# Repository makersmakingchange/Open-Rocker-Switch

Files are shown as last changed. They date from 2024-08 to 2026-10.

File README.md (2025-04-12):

<!--- Open Source Assistive Technology: GitHub Readme Template Version 1.2 (2024-May-27)  --->
<!---
This is a GitHub repository intended to act as a template for an open source assistive technology device. It is meant to contain all design files, build files, and documentation for the project. More information about how to use the template is available in the [Documentation_Guide](/Documentation_Guide.docx). You can see examples of other Open AT Devices at the Makers Making Change [website](https://www.makersmakingchange.com/s/category/assistive-devices). 
--->
 
<!--- TITLE --->
# Open Rocker Switch
<!--- Should match the name of the GitHub repository. Choose something descriptive rather than whimsical.  --->

## Overview
<!--- A brief summary of the project. What it does, who it is for, how much it costs. --->
The Open Rocker Switch is an inexpensive 3D printable accessibility switch. The switch consists of two separate buttons that are activated by pressing on either side. This switch is comparable in size, activation force, and travel to the discontinued AbleNet Rocker Switch. The Open Rocker Switch has interchangeable button pieces and center divider pieces for users to customize and personalize their switch.

The device is comprised of off-the-shelf electronics and 3D printed parts. 

The Open Rocker Switch is open assistive technology (OpenAT). Under the terms of the open source licenses, the device may be built, used, and improved upon by anyone.

The overall cost of materials is about $14 (plus $8 for component shipping).

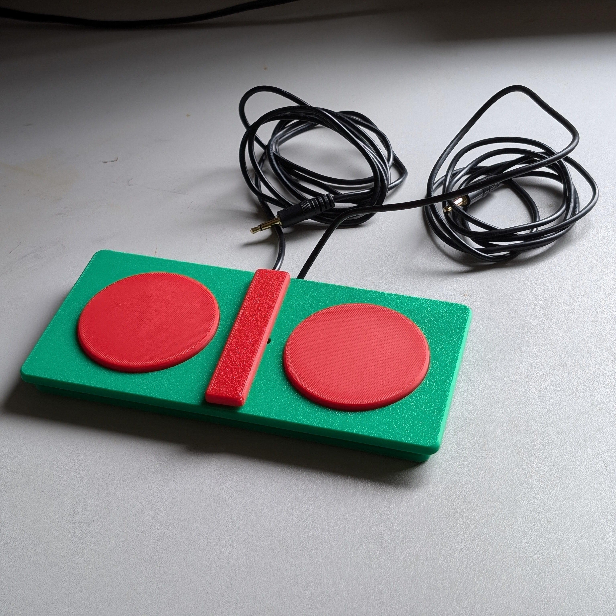
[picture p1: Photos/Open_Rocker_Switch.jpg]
Picture of Open Rocker Switch.


## Makers Making Change Assistive Device Library
https://www.makersmakingchange.com/s/product/open-rocker-switch/01tJR000000693uYAA

## How to Obtain the Device
### 1. Do-it-Yourself (DIY) or Do-it-Together (DIT)

This is an open-source assistive technology, so anyone is free to build it. All of the files and instructions required to build the device are contained within this repository. Refer to the Maker Guide below.

### 2. Request a build of this device

You may also submit a build request through the [Makers Making Change Assistive Device Library Listing](https://www.makersmakingchange.com/s/product/open-rocker-switch/01tJR000000693uYAA) to have a volunteer maker build the device. As the requestor, you are responsible for reimbursing the maker for the cost of materials and any shipping.

### 3. Build this device for someone else

If you have the skills and equipment to build this device, and would like to donate your time to create the device for someone who needs it, visit the [MMC Maker Wanted](https://makersmakingchange.com/maker-wanted/) section.

## Build Instructions
<!--- Outline the major steps required to create a build --->

### 1. Read through the Maker Guide

The [Maker Guide](/Documentation/Open_Rocker_Switch_Maker_Guide.pdf)  contains all the necessary information to build this device, including tool lists, assembly instructions, programming instructions (if applicable) and testing.

### 2. Order the Off-The-Shelf Components
The [Bill of Materials](/Documentation/Open_Rocker_Switch_BOM.xlsx) lists all of the parts and components required to build the device.

### 3. Print the 3D Printable components
All of the files and individual print files can be found in the [/Build_Files/3D_Printing_Files](/Build_Files/3D_Printing_Files/) folder.

### 4. Assemble the Open Rocker Switch
Reference the Assembly Guide section of the [Maker Guide](/Documentation/Open_Rocker_Switch_Maker_Guide.pdf) for the tools and steps required to build the device.

## How to improve this Device
As open source assistive technology, you are welcomed and encouraged to improve upon the design. 

## Files
### Documentation
<!--- Update the name, link, and version for documentation --->
| Document             | Version | Link |
|----------------------|---------|------|
| Design Rationale     | 2.2     | [Open_Rocker_Switch_Design_Rationale](/Documentation/Open_Rocker_Switch_Design_Rationale.pdf)     |
| Maker Guide          | 2.2     | [Open_Rocker_Switch_Maker_Guide](/Documentation/Open_Rocker_Switch_Maker_Guide.pdf)     |
| Bill of Materials    | 2.2     | [Open_Rocker_Switch_Bill_of_Materials](/Documentation/Open_Rocker_Switch_BOM.xlsx)     |
| User Guide           | 2.2     | [Open_Rocker_Switch_User_Guide](/Documentation/Open_Rocker_Switch_User_Guide.pdf)    |
| Changelog            | 2.2     | [Changelog](CHANGES.txt)     |

### Design Files
<!--- Include a copy of the original design files to facilitate easy editing and customization. Consider also including a generic format (e.g., STEP) --->
 - [CAD Files](/Design_Files/CAD_Design_Files)

### Build Files
<!--- Include a copy of the build files intended for manufacturing. This may include svg files for laser cutting, stl files for 3d printing, Gerber files for custom PCBs, and Arduino files for custom firmware. --->
 - [3D Printing Files](/Build_Files/3D_Printing_Files)

## License
<!--- Add the year(s) for the copyright and the Designer Name. You may use the standard set of open licenses or choose your own for the hardware, software, and accompanying materials. --->
Copyright (c) 2024 Neil Squire Society.

This repository describes Open Hardware:
 - Everything needed or used to design, make, test, or prepare the Open Rocker Switch is licensed under the [CERN 2.0 Weakly Reciprocal license (CERN-OHL-W v2) or later](https://cern.ch/cern-ohl ) .
 - Accompanying material such as instruction manuals, videos, and other copyrightable works that are useful but not necessary to design, make, test, or prepare the <Device-Name> are published under a [Creative Commons Attribution-ShareAlike 4.0 license (CC BY-SA 4.0)](https://creativecommons.org/licenses/by-sa/4.0/) .

You may redistribute and modify this documentation and make products using it under the terms of the [CERN-OHL-W v2](https://cern.ch/cern-ohl).
This documentation is distributed WITHOUT ANY EXPRESS OR IMPLIED WARRANTY, INCLUDING OF MERCHANTABILITY, SATISFACTORY QUALITY AND FITNESS FOR A PARTICULAR PURPOSE.
Please see the CERN-OHL-W v2 for applicable conditions.

Source Location: https://github.com/makersmakingchange/Open-Rocker-Switch

## Attribution
<!--- Provide any necessary attribution for designs or components that are included in the device or as part of the project. --->
The device was designed by Neil Squire Society/Makers Making Change. 

<!--- This is the attribution for the template. --->
The documentation template was created by Makers Making Change / Neil Squire Society and is used under a CC BY-SA 4.0 license. It is available at the following link: [https://github.com/makersmakingchange/OpenAT-Template](https://github.com/makersmakingchange/OpenAT-Template)

### Contributors
<!--- List the names of the people that contributed to the design. This could include the original source of the idea, designers, testers, documenters, etc. --->
Designers:
 - Gabriel Chu
 - Jake McIvor
 - Brad Wellington

---

<!-- ABOUT MMC START -->
## About Makers Making Change
[Makers Making Change Logo](https://www.makersmakingchange.com/)

Makers Making Change is a program of [Neil Squire](https://www.neilsquire.ca/), a Canadian non-profit that uses technology, knowledge, and passion to empower people with disabilities.

Makers Making Change leverages the capacity of community based Makers, Disability Professionals and Volunteers to develop and deliver affordable Open Source Assistive Technologies.

 - Website: [www.MakersMakingChange.com](https://www.makersmakingchange.com/)
 - GitHub: [makersmakingchange](https://github.com/makersmakingchange)
 - Bluesky: [@makersmakingchange.bsky.social](https://bsky.app/profile/makersmakingchange.bsky.social)
 - Instagram: [@makersmakingchange](https://www.instagram.com/makersmakingchange)
 - Facebook: [makersmakechange](https://www.facebook.com/makersmakechange)
 - LinkedIn: [Neil Squire Society](https://www.linkedin.com/company/neil-squire-society/)
 - Thingiverse: [makersmakingchange](https://www.thingiverse.com/makersmakingchange/about)
 - Printables: [MakersMakingChange](https://www.printables.com/@MakersMakingChange)

### Contact Us
For technical questions, to get involved, or to share your experience we encourage you to [visit our website](https://www.makersmakingchange.com/) or [contact us](https://www.makersmakingchange.com/s/contact).
<!-- ABOUT MMC END -->

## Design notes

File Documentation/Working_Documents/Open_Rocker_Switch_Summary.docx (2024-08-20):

# Overview

The Device Summary is intended to be a detailed summary of the device, product and maker information for the Open Rocker Switch, making it easier to add to the Makers Making Change website. It is intended for anyone who will view the device listing.

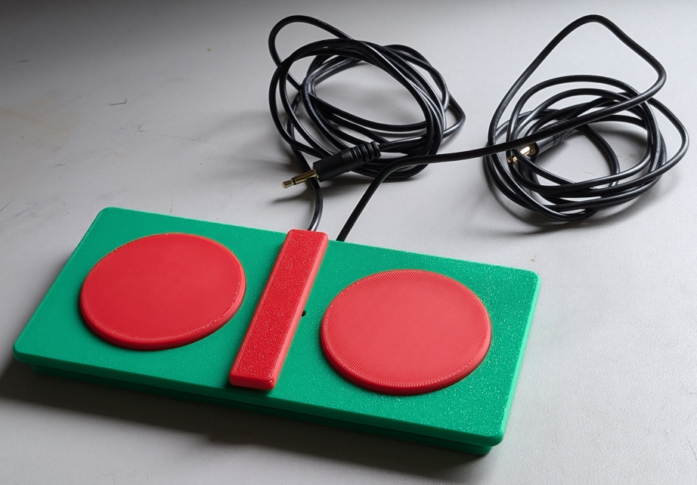
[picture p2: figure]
A photo of the Open Rocker Switch printed in green with red buttons and dividers

# Product Information

## Product Name

Open Rocker Switch

## Device Category

Mark any relevant categories with an “X”:

| Adapted Toys
| Aids for Daily Living (ADL)
X | Assistive Switches
X | Communication Aids (AAC)
X | Computer Access
| Environmental Controls
| Gaming
| Keyguard
| Kits
| LipSyncs
| Mounting
| Recreation and Leisure
| Seating and Positioning
| Switch Interfaces
| Writing Aids

## User Value Statement

If you are looking for an assistive switch to control two separate inputs on an accessible device, the dual action Open Rocker Switch might just be the two-in-one solution for you.

## Designer

Makers Making Change

# Device Information

## Overview

The Open Rocker Switch is a cost effective, 3D printed, dual action rocker switch that allows users to control dual input accessible devices.

# This switch is comparable in size, activation force, and travel to the discontinued AbleNet Rocker Switch. The Open Rocker Switch has interchangeable button pieces and center divider pieces for users to customize and personalize their switch.

## Disability Type

Select one or more disability types and mark with an “X”:

X | Agility / Dexterity
| Arthritis
X | Cognitive
| Hearing
X | Mobility
| Pain
| SCI
| Vision
| Other

## Disability Type Description

This device is designed for users of accessible switches, particularly those using devices that require dual inputs, such as scanning devices or morse code input.

## How To Use

The user presses on the buttons on either side of the central divider. The buttons activate the device connected to the corresponding mono cable.

## Estimated Cost

The estimated material cost of the device for a single build:

| $0 - $10
X | $11 - $25
| $26 - $50
| $51 - $100
| $101 - $250
| $250+

## Attribution

The Open Rocker Switch is inspired by the design of the now discontinued Ablenet Rocker Switch, originally created by TASH.

Design:

- Gabriel Chiu
- Jake McIvor
- Brad Wellington

# This switch is comparable in size, activation force, and travel to the discontinued AbleNet Rocker Switch. The Open Rocker Switch has interchangeable button pieces and center divider pieces for users to customize and personalize their switch.

# Maker Information

## Project Skills

Mark the required project skills with an “X”:

X | 3D Printing
| Custom PCB
| Electronics
| Laser Cutting
| Mechanics
| Software
X | Soldering
| Woodworking
| Other

## Skills Description

Hot glue to attach the buttons, 3D printing to create the components, soldering to attach the buttons to the cable, hand tools to trim parts and strip wires.

## Tools Needed

X | 3D Printer
X | Common Hand Tools
| Common Power Tools
| Laser Cutter
X | Soldering Iron
| Specialized Tooling

## Print time (hrs)

3

## Assembly time (hrs)

0.25

## Build Instructions

All parts are 3D printed. The buttons are bent and trimmed to shape, then the mono cables soldered to them. The buttons are hot glued to the switch base, then the cables cable tied in place. The buttons prints and divider are attached to the top rocker face of the switch, then the top face is connected to the bottom using the axle pin.

## Download Link

https://github.com/makersmakingchange/Open-Rocker-Switch /archive/refs/heads/main.zip

## Project Link

https://github.com/makersmakingchange/Open-Rocker-Switch

# License

## License

Hardware: CERN 2.0 Permissive license

Documentation: Creative Commons Attribution-ShareAlike 4.0

© 2024 by Neil Squire. This work is licensed under the CC BY SA 4.0 License: http://creativecommons.org/licenses/by-sa/4.0 Page 1 of 2

V2.2 | August 2024 Open Rocker Switch Summary

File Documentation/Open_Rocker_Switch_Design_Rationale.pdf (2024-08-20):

V2.2 | August 2024

## Open Rocker Switch

## DESIGN RATIONALE

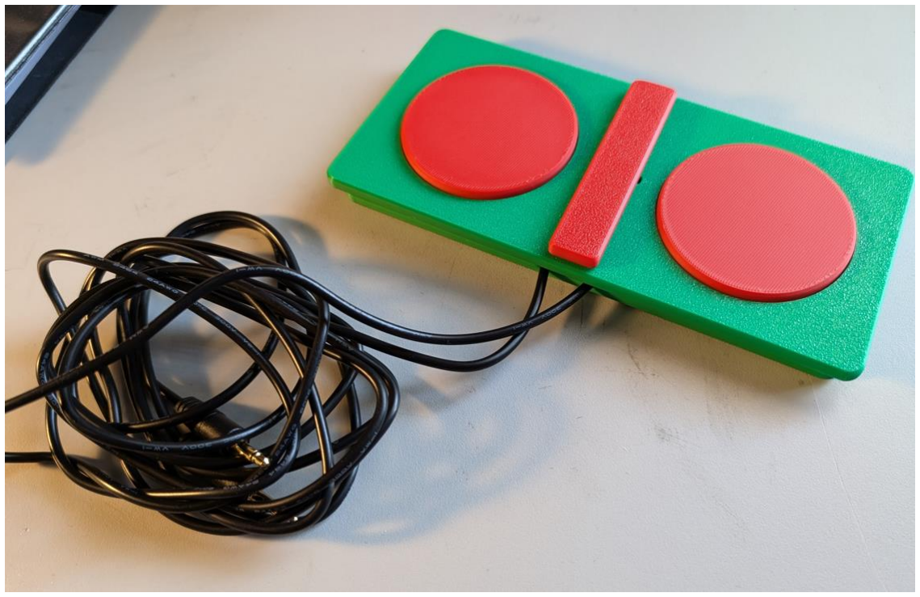
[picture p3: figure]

© 2024 by Neil Squire. (https://neilsquire.ca/)
This work is licensed under the CC BY SA 4.0 License: http://creativecommons.org/licenses/by-sa/4.0
Files available at https://github.com/makersmakingchange/Open-Rocker-Switch | Page 1 of 17

### Overview

The Design Rationale is intended to provide designers and maker information about the design process and design decisions behind the development of the Open Rocker Switch, a dual action rocker switch that is comparable in size, activation force, and travel to the discontinued AbleNet Rocker Switch

## DESIGN RATIONALE

Files available at https://github.com/makersmakingchange/Open-Rocker-Switch | Page 2 of 17

### Contents

Completion Checklist (DELETE BEFORE POSTING) | Error! Bookmark not defined.
Outline | 1
Introduction | 3
Research | 3
Requirements | 3
Goals | 3
Functional Requirements | 3
Non-functional Requirement | 3
Constraints | 3
Ideation | 4
Conceptual Design | Error! Bookmark not defined.
Concept 1 | Error! Bookmark not defined.
Concept 2 | Error! Bookmark not defined.
Concept 3 | Error! Bookmark not defined.
Prototyping | Error! Bookmark not defined.
Testing | 10
Detailed Design | 10
Opportunities for Improvement | Error! Bookmark not defined.

## DESIGN RATIONALE

Files available at https://github.com/makersmakingchange/Open-Rocker-Switch | Page 3 of 17

### Introduction

This design rationale is being put together for V2.2 of the device, and some information from the development has been lost.

A user of the AbleNet Rocker Switch was looking for a replacement switch after the one they were using was broken, but AbleNet had discontinued the switch. The Open Rocker Switch was developed as a open source replacement to meet the users needs.

The Open Rocker Switch is a low profile, low force switch that allows for controlling a device that requires multiple inputs, such as a scanning device or morse code input.

### Requirements

### Goals

G01 Open source switch comparable to the AbleNet Rocker Switch

### Functional Requirements

F01 | Same profile as the rocker switch
F02 | Same activation travel
F03 | Same activation force

### Non-functional Requirement

NF01 All parts must be available from the same supplier

### Constraints

C01 | Must be 3D printed
C02 | Must be manufacturable with common hand tools

### Commercially Available Options

Options that can be purchased but not made by a maker.

AbleNet Rocker Switch
Title / Name of device | Rocker Switch
Link | Discontinued
Author | AbleNet
Cost | $110 USD

## DESIGN RATIONALE

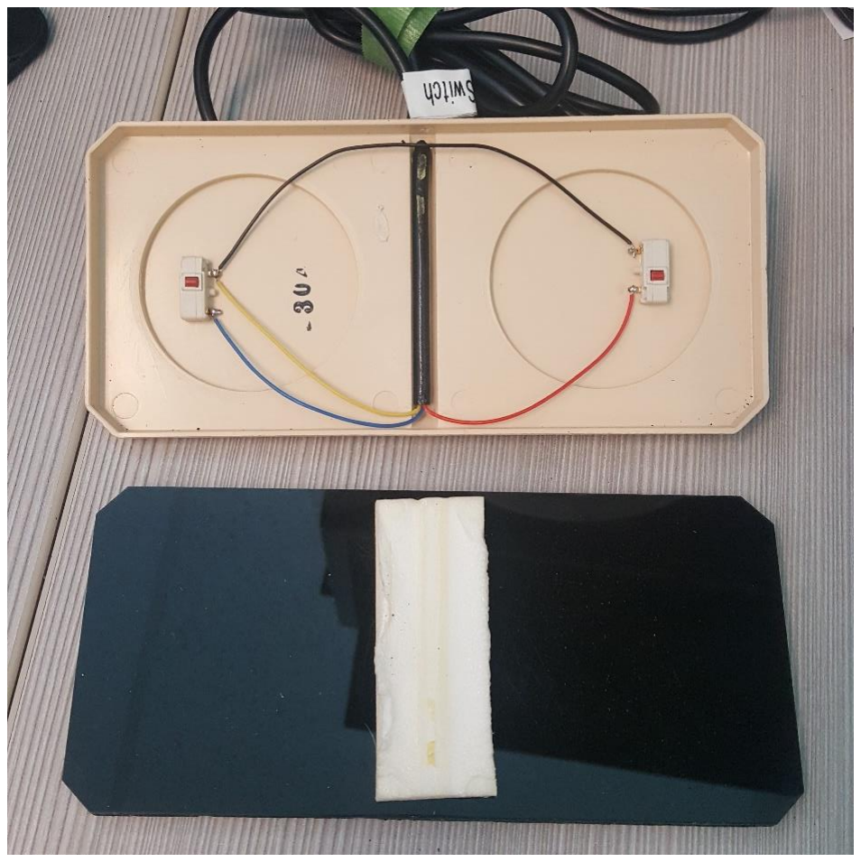
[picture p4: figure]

Files available at https://github.com/makersmakingchange/Open-Rocker-Switch | Page 4 of 17

The Rocker switch consisted of a base piece of acrylic, with a piece of two sided tape that acted as both an axle and a fixture for both sides. Two small switches were placed on the top under the buttons, and a stereo cable carried the signal out of the device.

Requirements Met | Requirements Unmet
The design of this device drove all requirements for the Open Rocker Switch | Availability

Useful Design Features
The user liked this device because it was low profile and low force, with two switch outputs.

### Ideation

The following is a compilation of all documents found in the ideation folder for this device.

## DESIGN RATIONALE

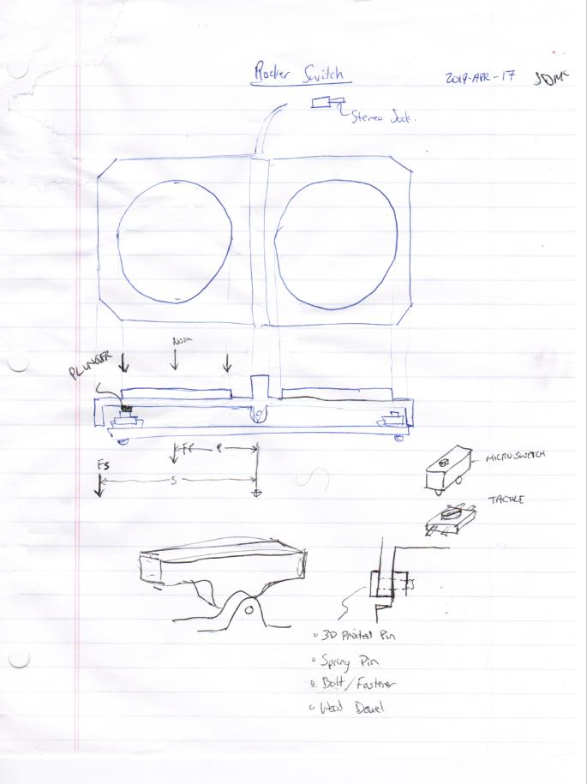
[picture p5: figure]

Files available at https://github.com/makersmakingchange/Open-Rocker-Switch | Page 5 of 17

## DESIGN RATIONALE

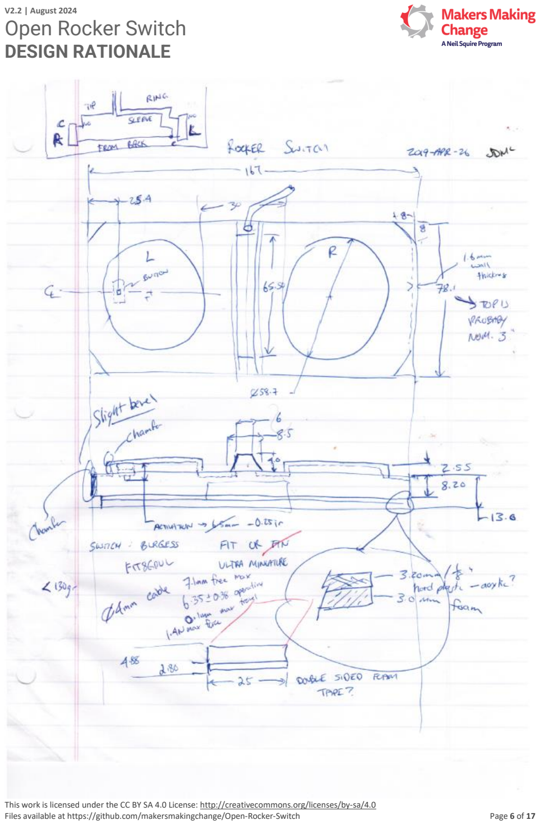
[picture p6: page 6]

Files available at https://github.com/makersmakingchange/Open-Rocker-Switch | Page 6 of 17

## DESIGN RATIONALE

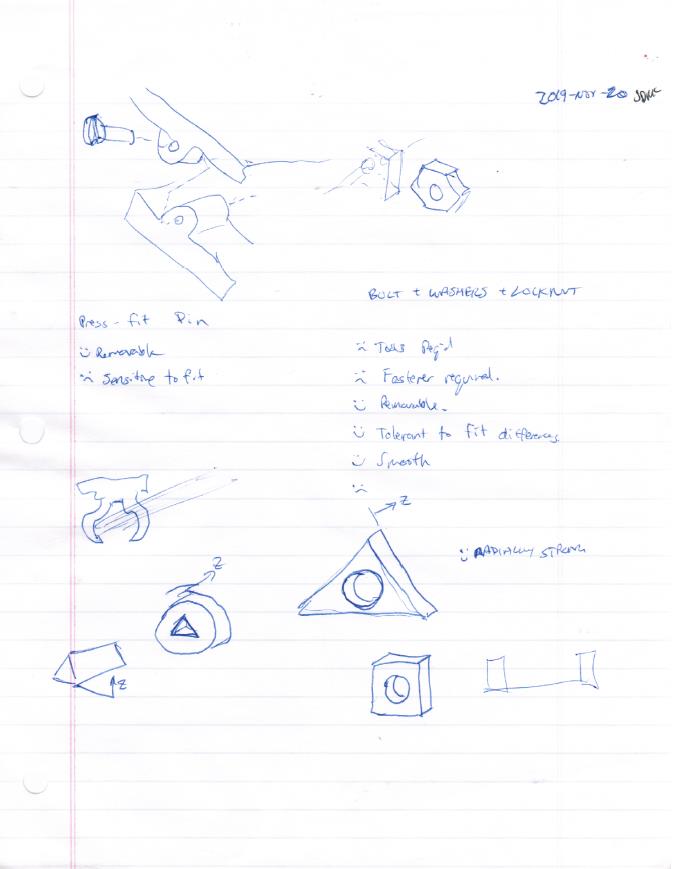
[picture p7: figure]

Files available at https://github.com/makersmakingchange/Open-Rocker-Switch | Page 7 of 17

## DESIGN RATIONALE

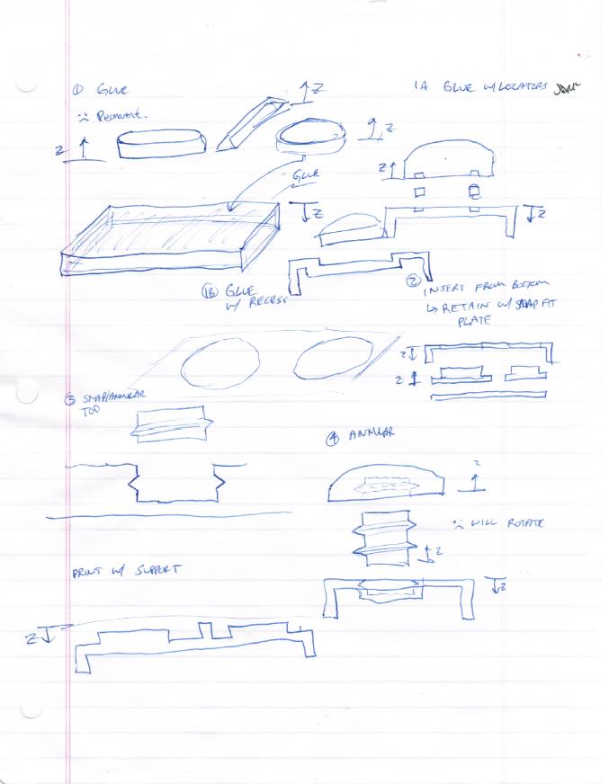
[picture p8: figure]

Files available at https://github.com/makersmakingchange/Open-Rocker-Switch | Page 8 of 17

## DESIGN RATIONALE

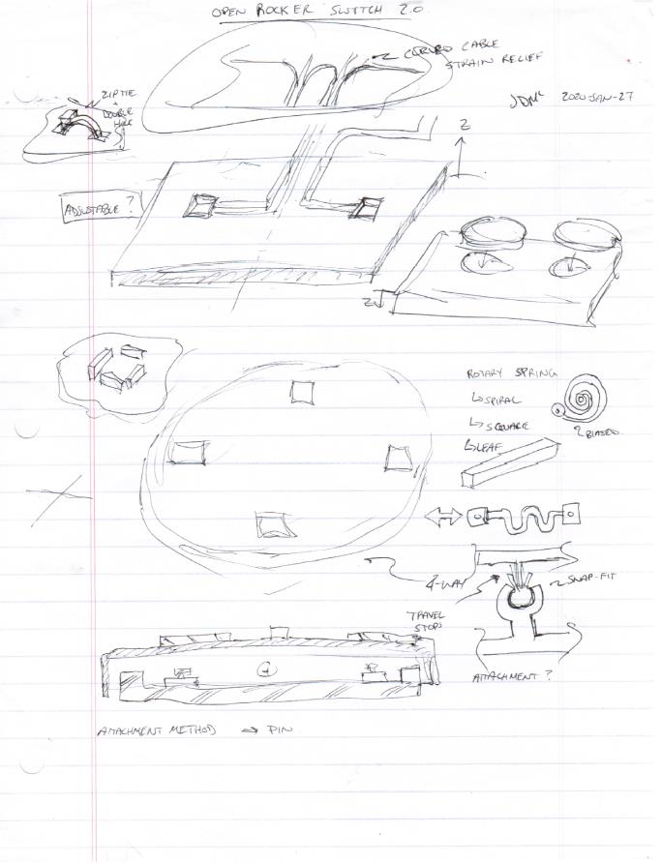
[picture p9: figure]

Files available at https://github.com/makersmakingchange/Open-Rocker-Switch | Page 9 of 17

## DESIGN RATIONALE

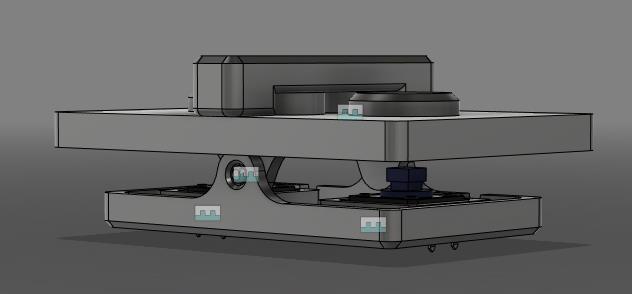
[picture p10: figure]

Files available at https://github.com/makersmakingchange/Open-Rocker-Switch | Page 10 of 17

List of Changes

- Optimize for 3d Printing
- Two separate mono cable instead of single stereo cable
- Better hinge
- Easier to assemble (and disassemble)
- Cable strain relief

Constraints

- Same basic size and shape as original
- Switch type
- Activation force

### Testing

### Testing Done on Version 1

- Tested the viability of using springs as a means of the return mechanism
- Results: Failed
- Springs Made the overall system too high to match the requirement of maintaining the form factor of the original switch by AbleNet
- Changes: Will use Switches as return mechanism used in V2
- Tested the rotation strength of a 3D printed axle

## DESIGN RATIONALE

Files available at https://github.com/makersmakingchange/Open-Rocker-Switch | Page 11 of 17
- Method: tested the strength of the axle during rotation of the switch by doing both a fast switching of the two sides and smashing the sides and center of the switch
- Results Failed
- The Axle holds up to the pressing on either end but fails when smashed in the middle due to the pegs sticking out and causing a stress concentration
- Tested the strength of the Axle pieces for assembly
- Method: Tested the bending strength of the axle parts to ensure that the parts can bend but not break to assembly the top and bottom
- Results: Passed
- Axle pieces hold up to assembly but need to test for upscaled version

## DESIGN RATIONALE

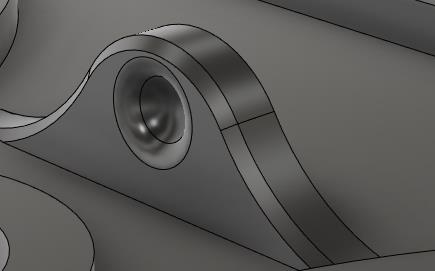
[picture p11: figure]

Files available at https://github.com/makersmakingchange/Open-Rocker-Switch | Page 12 of 17

### Testing Done on Version 2

- Tested Previous Axle design on this version
- Results: Failed
- Axle breaks on assembly
- Changes: changed to different design inspired from Simple switch tester clip
- Result from changes:
- Design proves to be better suited and makes assembly easier

▪
- Tested new Axle design
- Method: Tested the strength of the axle under normal operation and extreme operation by smashing the top surface of the switch.
- Results: Passed
- Easier to assemble and less prone to breaking and wearing out
- Tested Possibility of both buttons being pressed
- Method: Apply force on both ends of the switch and using a switch tester to test if both buttons can be actuated
- Results: Failed
- Both buttons can be pressed because of the flexibility of the PLA top
- Changes:
- Different material?
- Support to limit?
- Twist test

## DESIGN RATIONALE

Files available at https://github.com/makersmakingchange/Open-Rocker-Switch | Page 13 of 17
- Method: twisted the assembly to test the structure and see if it holds and if a button is not pressed when twisted
- Results: Failed
- Assembly holds but one of the switches activates because of how close the top is to the switches
- Changes:
- Tighter tolerance on the indents to limit the rotation of the assembly
- Possibly change the shape
- Smash test and button tests
- Method: Smashing the button with full force to test if the button is smashable
- Tested the amount of force required to activate the button
- Results: Passed
- The switch can handle being smashed without pieces breaking.
- Depends Heavily on strength of the switches
- Tested 3D printing Top piece without Support
- Method: Using the Cura Slicer
- Results: Failed
- Axle does not print well and middle keyed hole for divider has webbing that interferes with the assembly
- Tested Gluing method comparing super glue to hot glue for mounting switches
- Method: Compared hot glue to super glue by applying the glue to the switch mount cavity and testing the adhesion
- Result: Passed
- Hot glue is better for mounting the switches
- Comments:
- If possible, to get a tighter tolerance cut on the bottom of the switches, Super glue can be used.
- Tested Mounting method for securing for the 3.5 mm Plug wire
- Method: Compared Hot glue to super glue tested by putting both only at exit area
- Result: Passed
- Super Glue holds better but a different design may change that
- Comments:
- Need to apply pressure until glue sets or else the wire comes loose
- Better to apply super glue over the entire track
- Changes?
- Improved Cable track
- Improve Cable track for easier gluing
- Cable Tug Test
- Method: Tested the cable in handling being tugged by hand and tugged out of a 3.5mm jack in a computer (I used my own desktop computer I/O)
- Results: Passed

## DESIGN RATIONALE

Files available at https://github.com/makersmakingchange/Open-Rocker-Switch | Page 14 of 17
- May change but proven that a strain relief would be beneficial but not necessary and a strain relief may not fit in the form factor
- Drop Test
- Method: Dropping fully assembled switch from various heights to test durability and activation of switches during drop
- Results: Failed
- Switches activate on a 1-inch high drop but do not activate if shaken around by hand
- Dropped off desk at about 3ft high and assembly holds up
- Dropped 6ft high and assembly holds up
- Crush Test
- Method: Step on it and test the assembly without the switches
- Results: Passed
- Switch without buttons can withstand my weight on the switch
- The only thing that breaks is the keyed part on the top but does not affect the functionality of the switch during normal operation
- Divider becomes very loose
- Test slop with pins
- Method: Test different heights of the pins to test the amount of play that can be had for the switch
- Results:
- Can be changed to increase the travel of the switch but when using the hard point limits, there is no difference and will be a hinderance and the switch travel distance cannot be changed with just changing the pins alone
- Tested Increasing width of axle location
- Method: Test different spacing for the axle to test for better stability
- Result: Failed
- Both buttons can be pressed from the middle
- Tested Button Actuation
- Method: Tested whether the button can be actuated when pressed at every angle of the button like the MC60 switch
- Result: Failed
- Current Design cannot be pressed from all angles
- Changed buttons and top piece to have 4 points in the slot and changed hard stops to not interfere with the actuation
- Testing repair of broken axle
- Method: Tested whether fixing a broken axle piece with superglue is effective
- Result: Failed
- The glue must set for the total time of 24 hours and is not good for a quick fix
- The part is still volatile to breaking because the glue is trying to bond layers that are broken and delaminated

## DESIGN RATIONALE

Files available at https://github.com/makersmakingchange/Open-Rocker-Switch | Page 15 of 17

The current Open Rocker Switch has two primary problems that need a design rework. The current clip based connection is extremely stiff, resulting in the attachment points on the base occasionally breaking rather than clipping in, as well as cable routing/strain relief that can come undone easily and interfere with the motion of the switch.

### Design Requirements

Design Requirement | Verification Test
All 3D printed parts are printed with 6 walls | Inspection Test: Verify that 3D printed walls on all parts have 6 wall perimeter
All 3D printed Parts are printed with support | Test case: Verify in print settings that Supports are generated
Height of Switch does not exceed 13mm excluding divider and button height | Test Case: Measure that the height does not exceed 13mm
3D printed hard stop pegs contact the bottom of the switch, but the tactile buttons can still be activated | Test Case: with buttons placed, ensure that the tactile switches are activated, and the hard stop pegs limit travel

### Tested Clip Methods

In the previous development of the Open Rocker Switch, it appears that two different styles of clip were used to attach the top and bottom of the switch.

### 3D Printed Axle

The axle clip method uses a 3D printed axle to connect the two halves of the switch. Upon testing, this method was discarded due to fragility and replaced with the current clip design

### Current Clip Design

The current clip design consist of two protrusions on the top and bottom halves, with a bump on the bottom clips and a recess on the top clips. The top clips are reinforced to reduce flexibility while the bottom clips are allowed to flex. Once clipped in place, the bump and recess allow the top to rotate around the bump.

### Tested Cable Connections

As far as could be found in the existing design documentation, cable tracks with superglue were the only form of cable management/strain relief used in the original design

## DESIGN RATIONALE

Files available at https://github.com/makersmakingchange/Open-Rocker-Switch | Page 16 of 17

### Prototyping

### Clip

Since the functionality of the current clip is fine if it is successfully assembled, an effort was made to fix the current design before redesigning a new one.

To try and improve the clip, several versions of the bottom were printed with a looser tolerance between the bottom and top sections of the clip. This made it easier to clip the two halves together, but added an element of wobble between the two halves, where the two halves can be rotated roughly 5 degrees relative to each other. Adding a riding surface at the original spacing reduced this somewhat.

Another method of adding flex to the system was tested, by removing the rib on the top of the switch to increase its flexibility. This was found to be roughly the same as the looser tolerance version, but with the same amount of wobble as the original switch.

There was no scale available that could measure above 3kg, but the force required seems to be slightly above that with the tops clicking on shortly after the scale hit 3kg out. To attempt to compare the force required to clip each of the designs together, pairs of them were pressed equally with both hands, and comparing the force required for each of the. For the looser tolerance vs the removed ribs version, the looser tolerance clipped together at a slightly lower force than the removed ribs, and the original version took more force than the removed ribs version, roughly 3 times the difference in force between the tolerance version and the removed ribs version.

### Cable Management

To provide strain relief, a cable tie slot was added to the base at the end of each cable channel. To secure the cable into the channel without the use of superglue, a top was added to the cable channel. However, this top interfered with the top half of the switch, so it was pared down to just the start and finish of the channel, which kept the cable in the channel just as well. The clip near the side of the switch where the cables exit was removed, and replaced with a zip tie for better strain relief and to accommodate different sizes of cable. The first zip tie holes were kept, though they are currently unused. If using a cable that is over or undersized and the clip at the end of the cable routing doesn’t work, the second zip tie can be used to hold the cable in place.

### Cotter Pin

An alternative version of the rocker switch was created to remove the flexure clip element entirely. A cotter pin was developed, and the bump/recess on the top and bottom of the switch was replaced with a hole on both elements, and they were thickened significantly to remove the flexure and improve the strength. There was enough clearance between the two halves of the switch that the pin could be inserted and the switch assembled without changing the clearance between the two halves. The final assembly has the same amount of wiggle as the original design, but with significantly less force required in assembly. The cotter pin was later modified to add a small handle for removing the pin, as well as a

## DESIGN RATIONALE

Files available at https://github.com/makersmakingchange/Open-Rocker-Switch | Page 17 of 17

longer center pin to help with assembly and removal. Finally, the side prongs were turned 90 degrees at the end to prevent them from accidently being used as an axle and to aid in deflecting around the posts during assembly.

### Buttons

The buttons were modified with more ribs to remove the overhand when printing with the button surface facing up. A lower surface facing the button was tried, but it was found the current distance was near the minimum distance possible before the buttons would be jammed in the pressed position on assembly. Detents were added to the buttons, and matching bumps to the top rocking surface to lock the buttons in place once they were assembled. This flipping of the print surface allows buttons to be designed with patterns and designs.

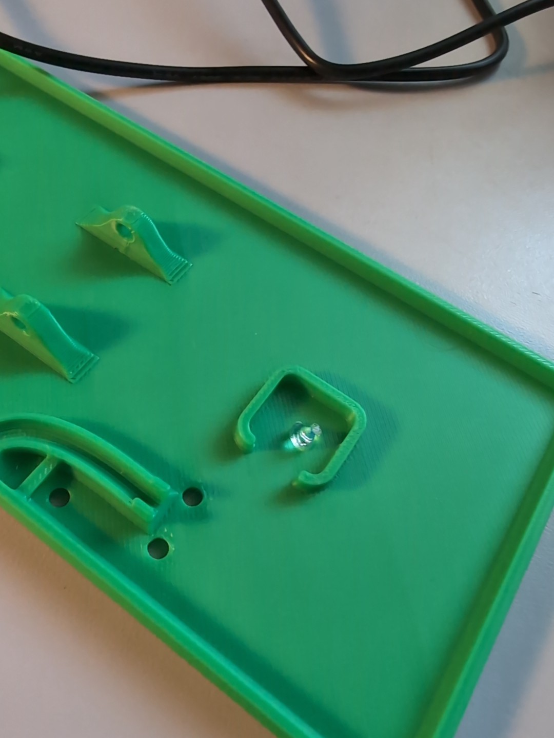
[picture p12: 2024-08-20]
Documentation/Working_Documents/Assets/Hot Glue Bead.jpg

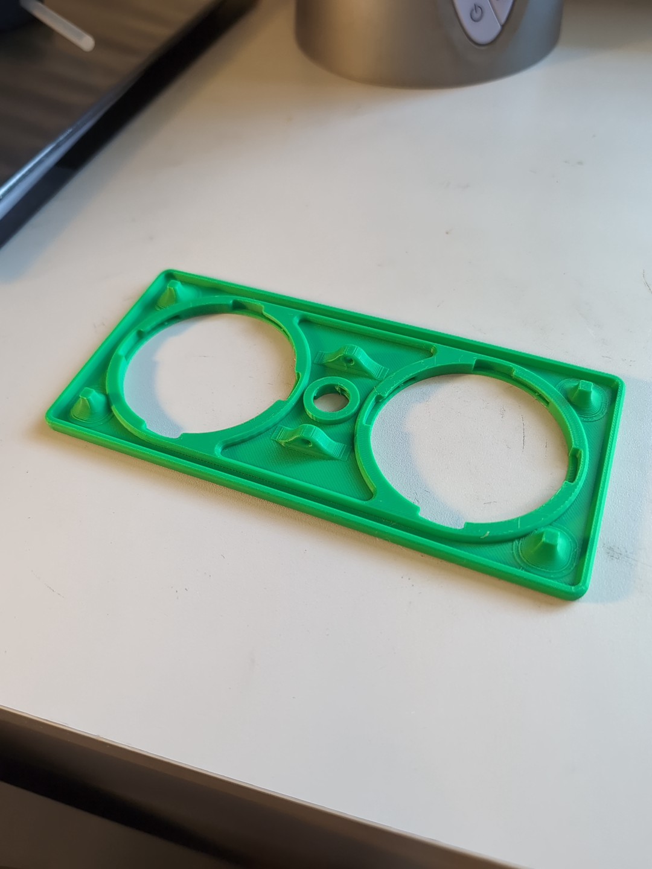
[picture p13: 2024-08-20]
Documentation/Working_Documents/Assets/ORS_Top Bottom.jpg

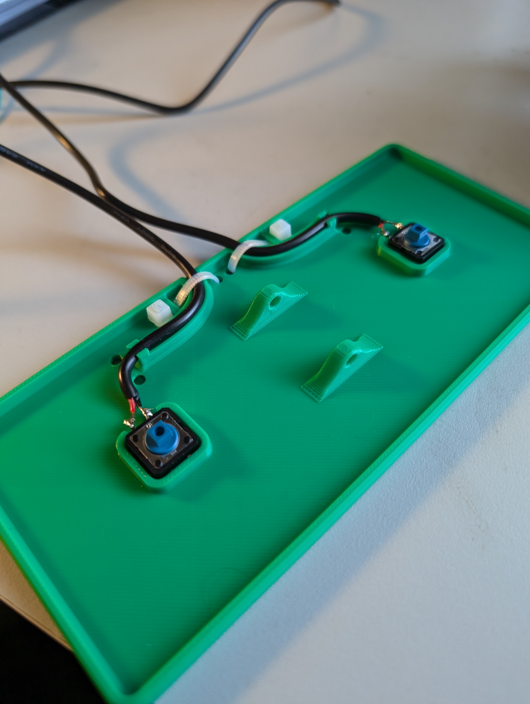
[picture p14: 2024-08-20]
Documentation/Working_Documents/Assets/trimmed cables.jpg

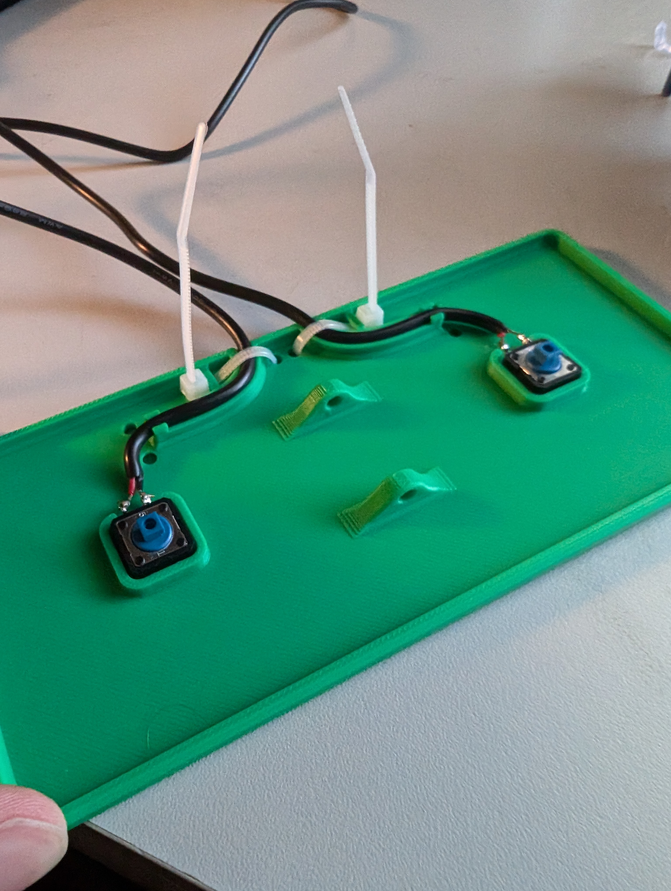
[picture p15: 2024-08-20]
Documentation/Working_Documents/Assets/Zip ties cables.jpg

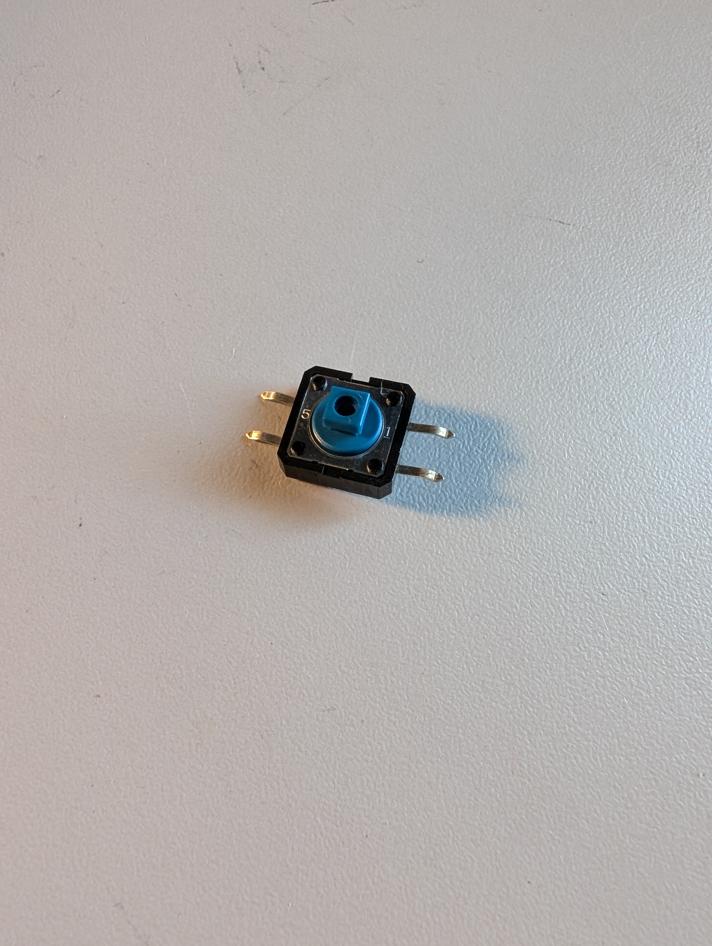
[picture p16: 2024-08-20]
Documentation/Working_Documents/Assets/Button Splayed.jpg

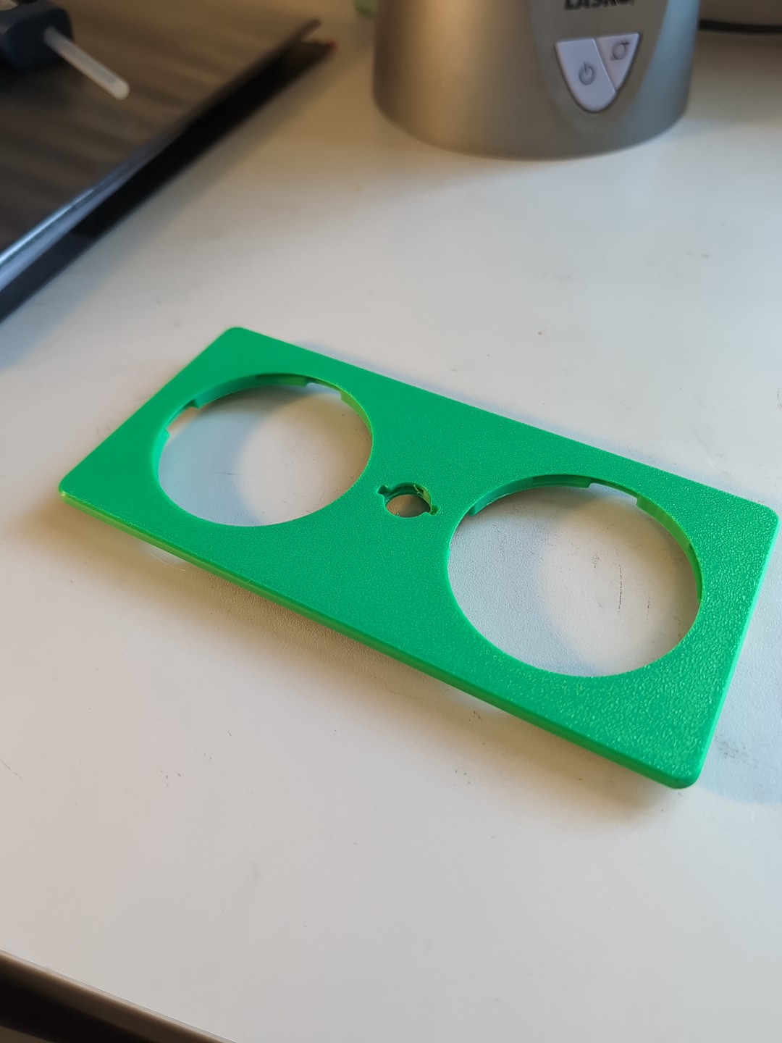
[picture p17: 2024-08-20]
Documentation/Working_Documents/Assets/ORS_Top Top.jpg

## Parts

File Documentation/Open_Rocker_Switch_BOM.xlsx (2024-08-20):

Device: | Open Rocker Switch
Version: | V2.2
Last Updated: | 2024-08-09
 |  |  |  |  |  |  |  | Total filament (g) |  | Unit Cost | Total Estimated Cost | Build Cost
 |  |  |  |  |  |  |  | 75 |  | $22.30 | $22.30
ID | Commercial Parts |  |  |  |  |  |  |  |  | $20.20 | $20.20
 | Part | Description |  | Manufacturer | Supplier | QTY / Device | QTY / PKG | PKGs | $/ PKG | $ / Device | Total Estimated Cost |  | Link
 | Button | Omron tactile switch SPST-NO |  |  | Digikey | 2 | 1 | 2 | $1.25 | $2.50 | $2.50 |  | https://www.digikey.ca/en/products/detail/omron-electronics-inc-emc-div/B3F-5050/368377
 | Cable Tie | Cable ties to secure cable |  |  | Digikey | 2 | 1 | 2 | $0.16 | $0.32 | $0.32 |  | https://www.digikey.ca/en/products/detail/3m/CT4NT18-M/2721151
 | Mono Cable | 3.5 mm mono cable - 6ft |  |  | Digikey | 2 | 1 | 2 | $4.69 | $9.38 | $9.38 |  | https://www.digikey.ca/en/products/detail/tensility-international-corp/10-00344/2350247
 | Shipping | Shipping for Digikey parts |  |  | Digikey | 1 | 1 | 1 | $8.00 | $8.00 | $8.00
 |  |  |  |  |  |  |  | 0 | $0.00 | $0.00 | $0.00
 | Custom PCB |  |  |  |  |  |  |  |  | $0.00 | $0.00
 | Part | Description |  | Manufacturer | Supplier | QTY / Device | QTY / PKG | PKGs | $/ PKG | $ / Device | Total Estimated Cost |  | Link
 |  |  |  |  |  | 0 | 0 | 0 | $0.00 | $0.00 | $0.00
 |  | Shipping |  |  |  | 0 | 0 | 0 | $0.00 | $0.00 | $0.00
 | 3D Printed Parts |  |  |  |  |  |  | 84 |  | $2.10 | $2.10
 | Part | Description | Filament Type | Filament | Color | QTY / Device | Mass (g) / Part | Total Mass | $ / kg | $ / Device | Total Estimated Cost |  | Link
 | ORS_Bottom | Base | PLA |  | Any | 1 | 32 | 32 | $25.00 | $0.80 | $0.80
 | ORS_Top | Rocker | PLA |  | Any | 1 | 29 | 29 | $25.00 | $0.73 | $0.73
 | ORS_Button | Button Surface | PLA |  | Any | 2 | 9 | 18 | $25.00 | $0.45 | $0.45
 | ORS_Divider | Button Divider | PLA |  | Any | 1 | 4 | 4 | $25.00 | $0.10 | $0.10
 | ORS_Pin | Axle Pin | PLA |  | Any | 1 | 1 | 1 | $25.00 | $0.03 | $0.03
 | Tools
 | Tool | Description |  | Manufacturer | Supplier |  |  |  |  |  |  |  | Link
 | Soldering Iron | For connecting electronics
 | Flush Cutters | For cutting wires and trimming plastic
 | Hot Glue Gun | For securing the buttons
 | Wire Strippers | For stripping wire insulation
 | Alternatives
 | Part | Description |  | Manufacturer | Supplier | QTY / Device | QTY / PKG | PKGs | $/ PKG | $ / Device | Total Estimated Cost |  | Link
 | Mono Cable | Alternative cheaper mono cable |  |  | Prime Cables | 1 | 1 | 1 | $2.29 | $2.29 | $2.29 |  | https://www.primecables.ca/p-370665-cab-aud-200-all-35mm-18-inch-mono-ts-male-to-male-28awg-ft4-cable-black

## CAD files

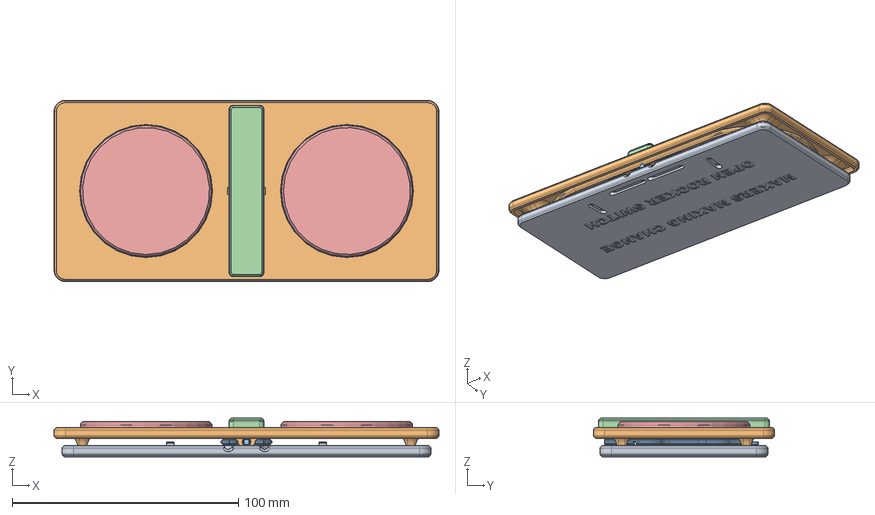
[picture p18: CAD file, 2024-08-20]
Design_Files/CAD_Design_Files/Step/ORS_Assembly.step
170.0 x 80.0 x 17.0 mm
ORS_Bottom_Piece_Cotter_Pin
ORS_Top_Piece_Cotter_Pin
Cotter Pin
ORS_Divider
ORS_Button_Piece_Flip x 2

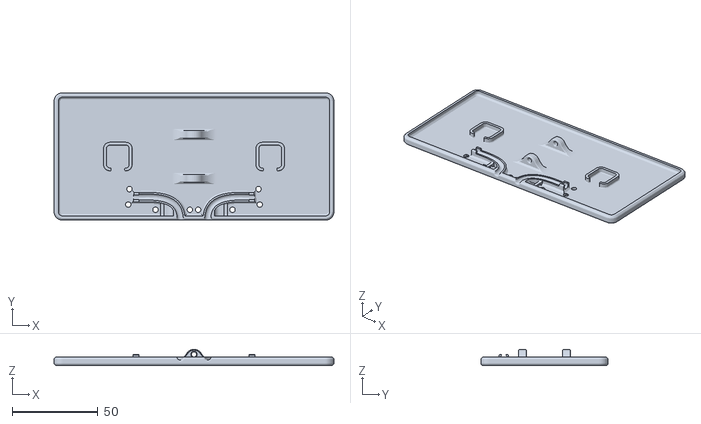
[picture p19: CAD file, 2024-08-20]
Build_Files/3D_Printing_Files/ORS_Bottom.stl
163.0 x 74.2 x 9.50

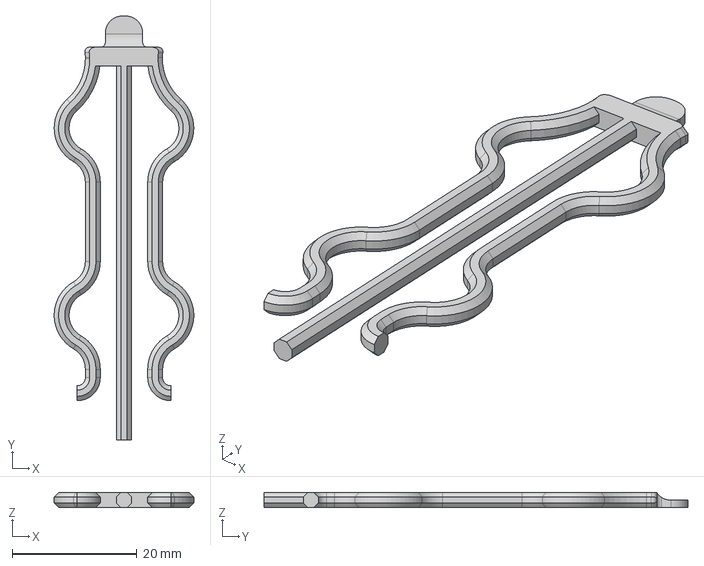
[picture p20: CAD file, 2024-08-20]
Design_Files/CAD_Design_Files/Step/ORS_Pin.step
22.4 x 68.0 x 2.40 mm

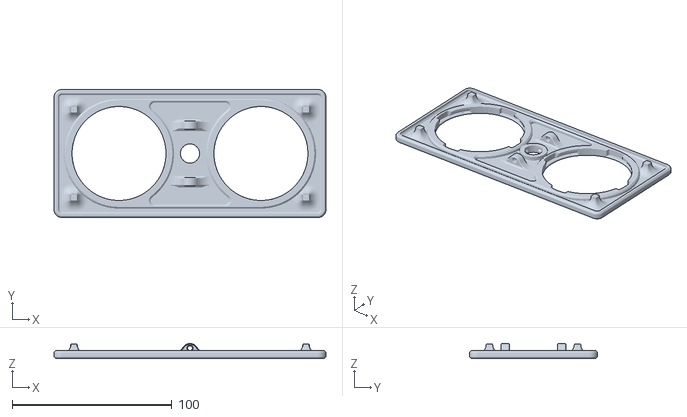
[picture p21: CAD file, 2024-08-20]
Build_Files/3D_Printing_Files/ORS_Top.stl
170.0 x 80.0 x 9.50

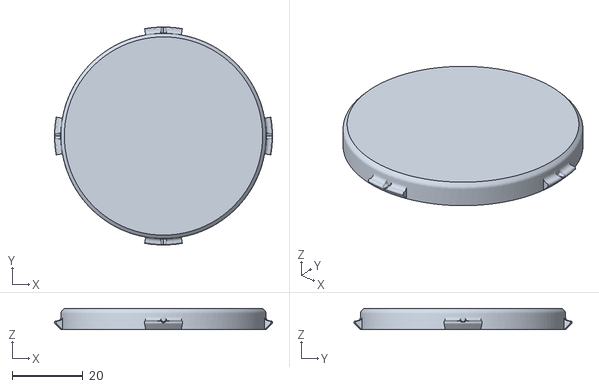
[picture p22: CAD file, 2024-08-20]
Build_Files/3D_Printing_Files/ORS_Button.stl
61.7 x 61.7 x 6.00

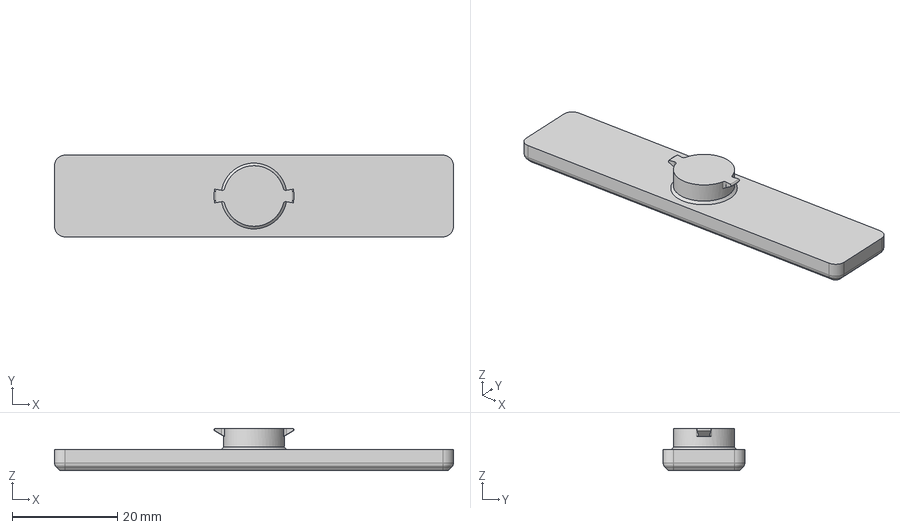
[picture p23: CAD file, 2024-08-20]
Design_Files/CAD_Design_Files/Step/ORS_Divider.step
75.7 x 15.5 x 8.00 mm

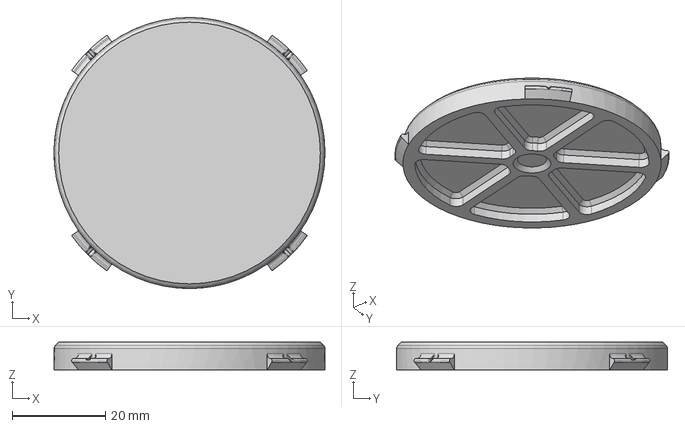
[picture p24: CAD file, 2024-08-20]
Design_Files/CAD_Design_Files/Step/ORS_Button.step
58.1 x 58.1 x 6.00 mm

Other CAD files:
Build_Files/3D_Printing_Files/ORS_Pin.stl
Design_Files/CAD_Design_Files/Step/ORS_Bottom.step
Build_Files/3D_Printing_Files/ORS_Divider.stl
Design_Files/CAD_Design_Files/Step/ORS_Top.step
Design_Files/CAD_Design_Files/Fusion/ORS_Bottom.f3d
Design_Files/CAD_Design_Files/Fusion/ORS_Button.f3d
Design_Files/CAD_Design_Files/Fusion/ORS_Divider.f3d
Design_Files/CAD_Design_Files/Fusion/ORS_Pin.f3d
Design_Files/CAD_Design_Files/Fusion/ORS_Top.f3d

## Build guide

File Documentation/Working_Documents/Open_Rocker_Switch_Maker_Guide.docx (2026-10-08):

# Overview

This document contains the necessary information to build the Open Rocker Switch, a two switch rocker style device, which can be activated by pressing the buttons on either side.

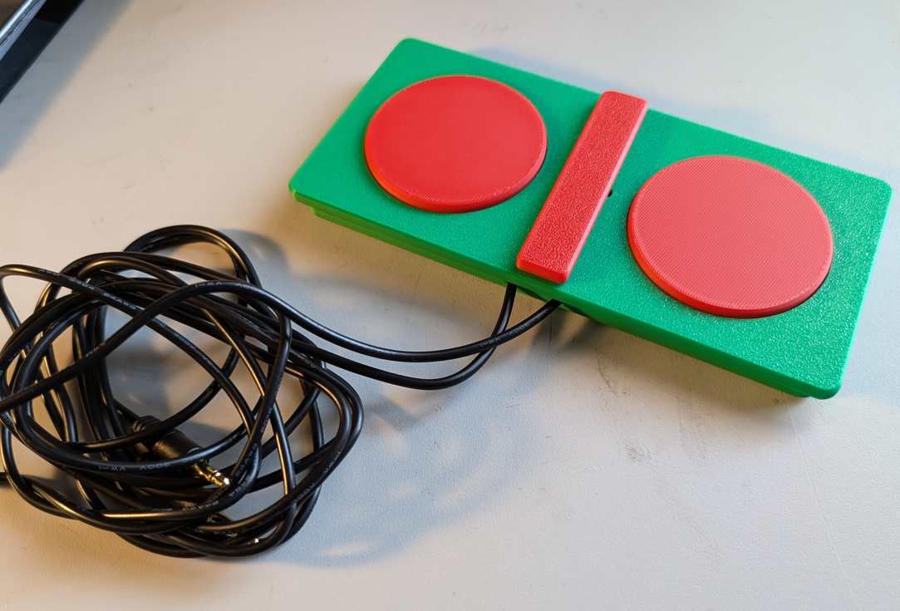
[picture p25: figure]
Open Rocker Switch, it is a green body with two red circles and a red line in the middle. There are two black cables coming out of it.

Contents

# Maker Checklist

This list provides an overview of the steps required to build and deliver the Open Rocker Switch

## Maker To Do List

- Read through the Maker Guide to become familiar with required components, tools, supplies, safety gear, and overall assembly steps.
- Talk to the User about customization options
  - Buttons and the divider can be printed in a different colour from the switch body
  - Buttons can be modified to be textured or have designs on them
  - How they would like to receive the “User Guide” (PDF or physical copy)
- Order hardware components
- Gather tools, supplies, and safety equipment.
- Assemble the device
- Test the Open Rocker Switch
- Print “User Guide” (if the User would like a physical copy)

## Items to Give to User

- Assembled and tested Open Rocker Switch
- “User Guide”

# Tool List

## Tools / Equipment

Tool ID | Description | Required / Recommended | Notes
T01 | Soldering Iron | Required | Soldering buttons
T02 | Flush Cutters | Required | Cutting and trimming
T03 | Hot Glue Gun | Required | Attaching Buttons
T04 | Wire Strippers | Required | Stripping wire

## Supplies

Supplies ID | Description | Quantity | | Notes
S01 | Solder | 4 solder joints | Soldering switches to cable
S02 | Hot Glue | 2 small dabs | Securing buttons to device

## Personal Protective Equipment (PPE)

PPE ID | Description | Notes
P01 | Safety glasses | Protecting your eyes

# Customization Guide

The device can be printed in the user’s desired colour.

The buttons can be modified in Fusion 360 or another modeling program to add texture, patterns, or designs.

# 3D Printing Guide

The device was originally printed on a Bambu P1S using Bambu Studio

All default settings were used.

## 3D Printing Summary

Metrics | Single Unit
Total Print Time (hour min) | 2h25min
Total Number of Components | 6
Typical Total Mass (g) | 84g
Typical Number of Print Setups | 2

## 3D Printing Settings

Note that the 3D printing material should be assumed to be PLA unless otherwise noted in the table below.

Print File Name | Qty | Total Print Time (hr:min) | Mass (g) | Infill (%) | Support(Y/N) | Layer Height/ Nozzle Diameter(mm) | Notes
ORS_Top.stl | 1 | 0:54 | 29 | 20 | N | 0.2/0.4
ORS_Bottom.stl | 1 | 0:52 | 32 | 20 | N | 0.2/0.4
ORS_Button.stl | 2 | 0:15 | 9 | 20 | N | 0.2/0.4
ORS_Divider.stl | 1 | 0:07 | 4 | 20 | N | 0.2/0.4
ORS_Pin.stl | 1 | 0:02 | 1 | 20 | N | 0.2/0.4

## Post-Processing

Inspect the 3D printed parts for any printing defects, sharp edges, or burrs. Sharp edges and burrs can be removed with sanding or deburring tools.

## Examples of Quality Prints

Compare your 3D prints to the images here. If there are significant differences, you may need to reprint the part.

Open Rocker Switch Prints

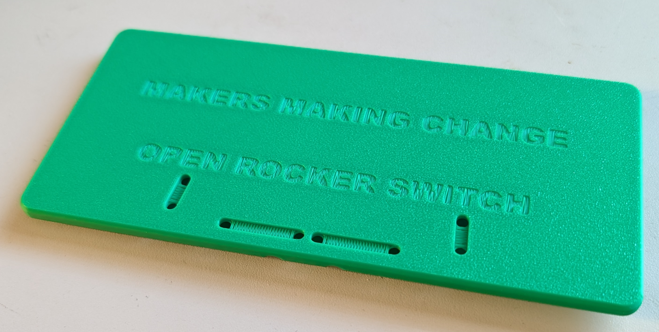
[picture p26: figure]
Bottom face of the bottom piece of the rocker switch

ORS_Bottom.stl

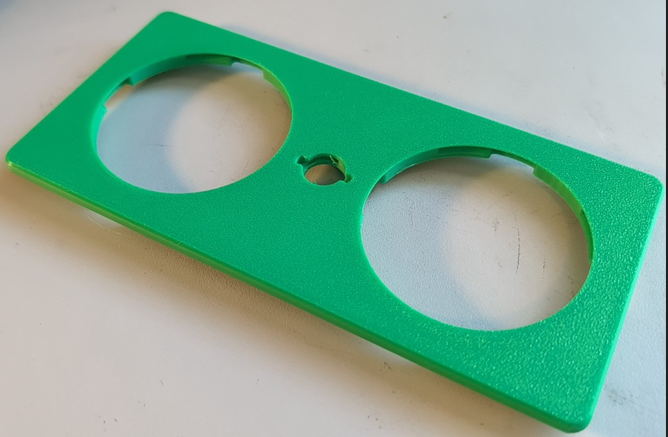
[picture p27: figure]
Top face of top piece of the switch printed in green

ORS_Top.stl

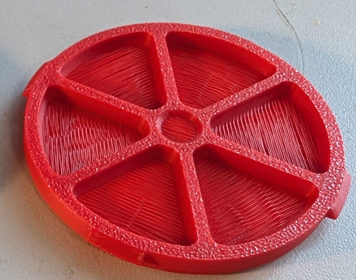
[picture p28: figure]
Bottom face of the button printed in red

ORS_Button.stl

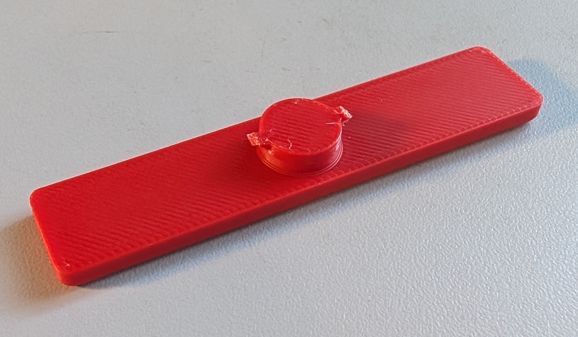
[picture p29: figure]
Bottom face of the divider printed in red

ORS_Divider.stl

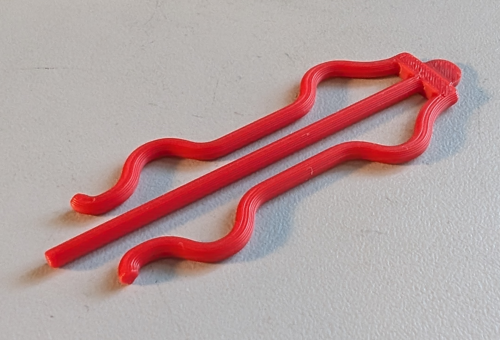
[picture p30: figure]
Cotter pin printed in red

ORS_Pin.stl

# Maker Component List

Open Rocker Switch
A01 | | ORS_Bottom | QTY: 1 | | A02 | | Button | QTY: 2 | A03 | Mono Cable | | QTY: 1
A04 | Zip Tie | | | QTY: 2 | A05 | ORS_Pin | | QTY: 1 | A06 | | ORS_Top | | QTY: 1
A07 | ORS_Divider | | | QTY: 1 | A08 | ORS_Button | | QTY: 2

# Assembly Guide

## Open Rocker Switch

### Open Rocker Switch Required Tools and Supplies

- T01: Soldering Iron
- T02: Flush Cutters
- T03: Hot Glue Gun
- T04: Wire Strippers

### Open Rocker Switch Required Personal Protective Equipment (PPE)

- P01: Eye Protection

### Open Rocker Switch Assembly Steps

#### Step A-01: Trim switch leads

Use a flush cutter to trim off the leads on one side of the tactile switch (A02). Make sure the leads are cut flush against the side of the switch and do not extend below the bottom of the switch.

#### Step A-02: Straighten remaining switch leads

Straighten the remaining switch leads, ensuring they stick straight out from the side of the switch. Use the needle nosed pliers, if necessary.

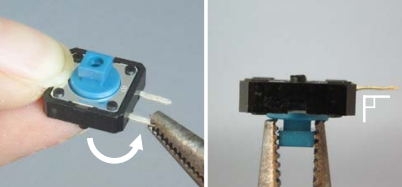
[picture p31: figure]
Bending the remaining leads of the tactile switch and showing them sticking straight out from the switch.

#### Step A-03: Trim mounting lugs

Use the flush cutters to trim the plastic mounting lugs (the plastic cylinders) off the bottom of the switch. Make sure the lugs are cut flush, with no remaining bumps.

#### Step A-04: Cut the mono cable in half

Take the mono cable (A03) and cut it in half using flush cutters (T02).

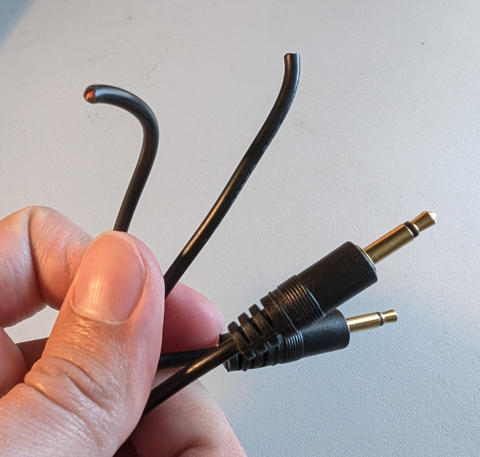
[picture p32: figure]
A mono cable that has been sliced in half in the middle

#### Step A-05: Strip the mono cable

Use the wire strippers (T04) to strip about 2 cm from the end of the mono cable, exposing the inner two wires. Twist the stranded wire together.

The inner wire colours may differ depending on the mono cable. Some may have one stranded wire and one coated wire, or have two coated wires. If you have two coated wires, do not twist any wires together at this step.

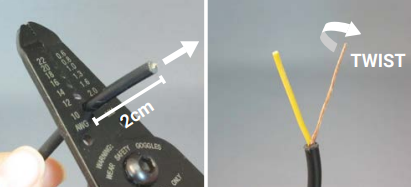
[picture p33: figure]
Stripping the mono cable and twisting the stranded wire together.

#### Step A-06: Strip the inner wire(s)

Strip about 1.5 cm of insulation from the end of the inner coated wire. Twist the wire strands from that wire together. Repeat this for the other coated wire, if both inner wires were coated.

The wire strands from each inner wire should not be touching each other or twisted together.

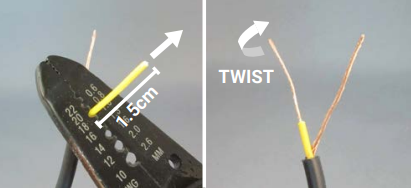
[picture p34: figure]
Stripping the inner coated wire and twisting the strands together.

#### Step A-07: Wrap wires around switch leads

Hold the mono cable behind the switch and wrap one wire around one switch lead and the other wire around the other switch lead. Which wire is connected to which lead does not matter, just make sure the wires and leads do not touch each other, or the switch will be short circuited. Needle nosed pliers may help with wrapping the wires.

#### Step A-08: Fix orientation of cable

Hold the switch in place and bend the mono cable around so it sits between the leads of the switch.

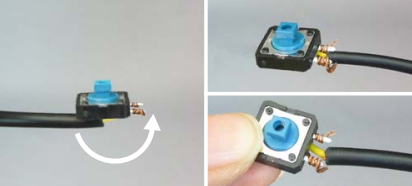
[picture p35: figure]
Flipping the mono cable so it runs between the leads of the switch.

#### Step A-09: Solder switch joints

Solder the cable wires to the switch leads with the soldering iron (T01). Once soldered, the wires should not slip off the switch leads.

Once the switch is soldered, test the switch using a switch tester. Make sure it activates the switch tester when the switch is pressed, and turns off when the switch is not being pressed.

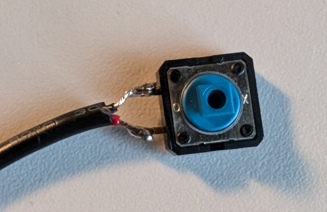
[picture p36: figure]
A button with both mono cable leads soldered on

#### Step A-10: Hot glue the buttons to the base

Using a pinhead sized bead of hot glue, glue both switches to the square switch slots in the base of the switch(A01) using the hot glue gun (T03).

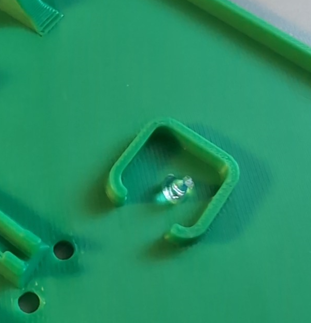
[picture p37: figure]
The switch slot with a pinhead sized dab of hot glue
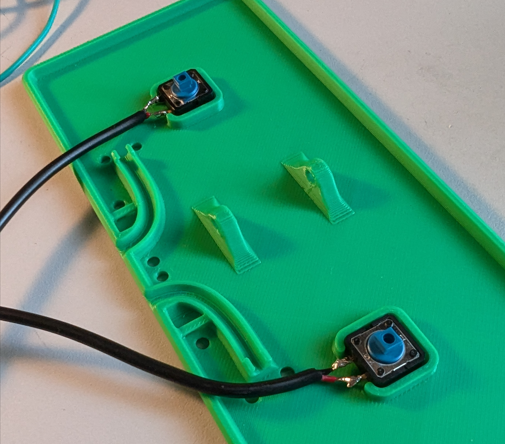
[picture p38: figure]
Both switches glued in place on the base

#### Step A-11: Insert the cable ties

Pass the tail of the cable ties(A04) through the bridge towards the centre of the switch. Lay the cables along the track on the base

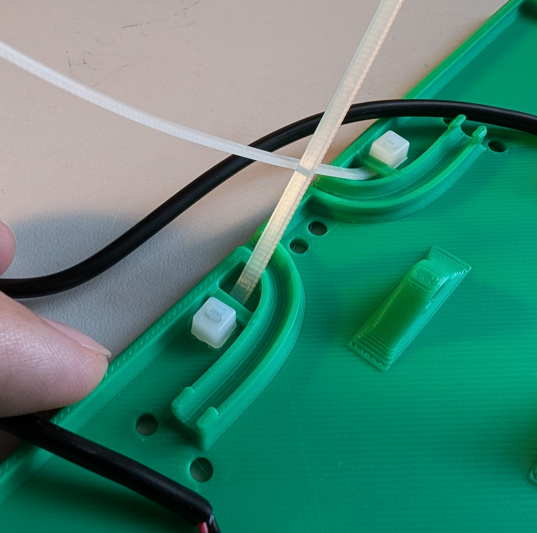
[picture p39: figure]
The zip ties passed through the slots on the base

#### Step A-12: Loop the cable ties

Pass the tail ends of the cable ties over the cable and down through the holes at the centre of the switch. Pass them along the track on the base and up through the second hole, through the head of the cable tie.

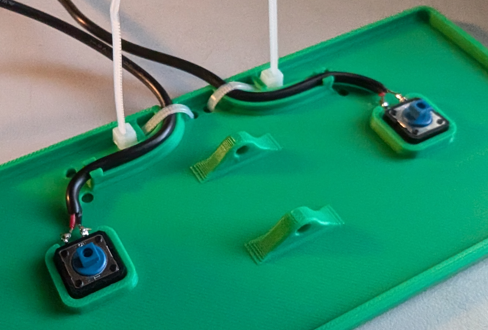
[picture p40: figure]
The cable tie assembly after tightening the zip ties
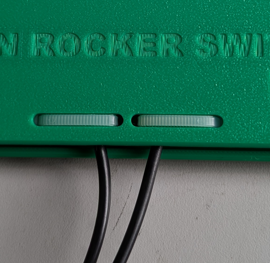
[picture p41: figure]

#### Step A-13: Tighten and trim the cable ties

Pull the cable ties tight until the cables are locked in place, then trim the tails of the cables flush with the head of the tie.

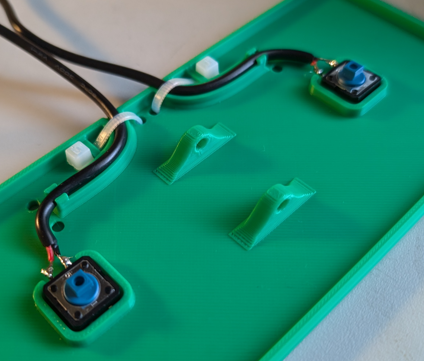
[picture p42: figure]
The assembled bottom with cable tie ends trimmed

#### Step A-14: Attach the divider to the top

Place the divider(A07) sideways into the slot on the top of the top piece of the switch(A06), and rotate it 90 degrees to lock it in place.

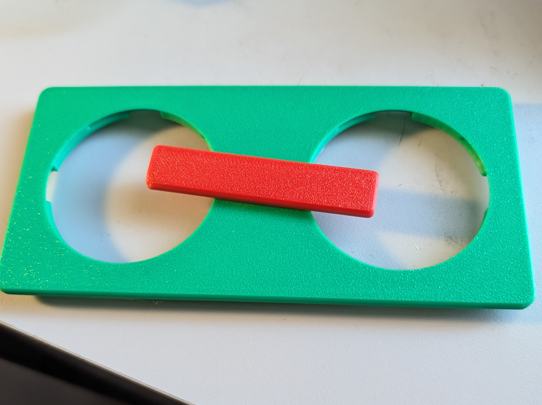
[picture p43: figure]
The divider dropped in place
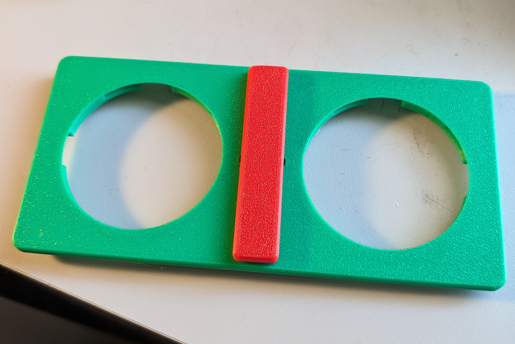
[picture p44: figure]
The divider rotated and locked in the correct position

#### Step A-15: Attach the buttons to the top

Flip the top assembly over, and place the buttons(A08) in both of the slots int the bottom. Twist each button 45 degrees until they lock in place.

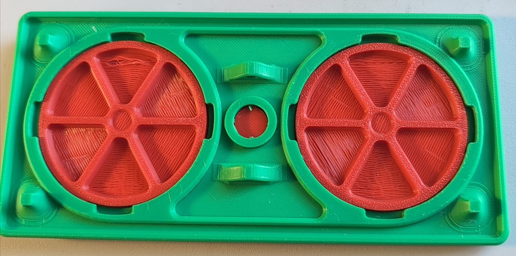
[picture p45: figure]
The buttons after they have been rotated and assembled in place

#### Step A-16: Pin the two halves of the switch together

Take the top and bottom assemblies and line up the holes on the posts on each. Take the pin(A05), and pass it through the holes from the far side towards the cables until you feel the pin click into place.

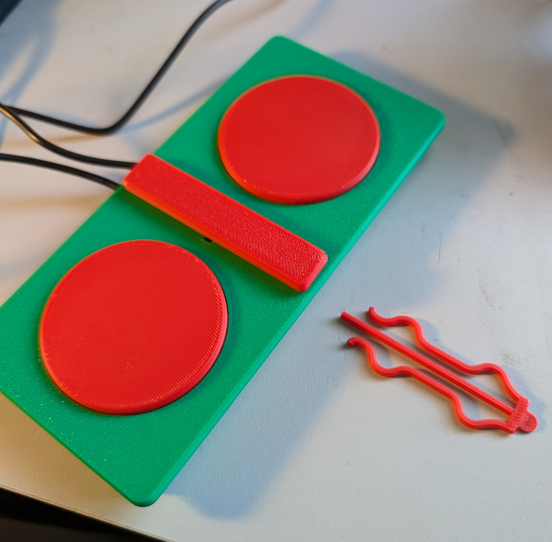
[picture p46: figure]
The two halves of the switch lying on top of each other with the pin in place showing the direction it would assemble
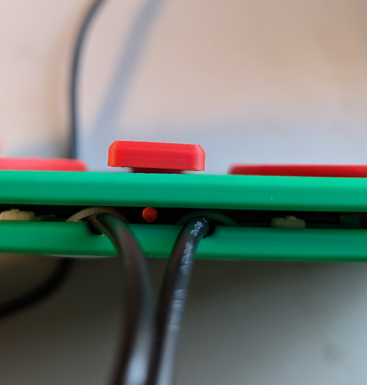
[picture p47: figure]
A close up of the inside of the switch showing the pin assembled in place

#### Step A-17: Test the assembled switch

Use a switch tester or a switch adapted device to test both of the cables coming out of the device. The switch tester should turn on when the switch is pressed, and turn off when the switch is not being pressed. If it does not work as expected, see the troubleshooting section.

If it works as expected, the switch is complete!

# Assembled Switch

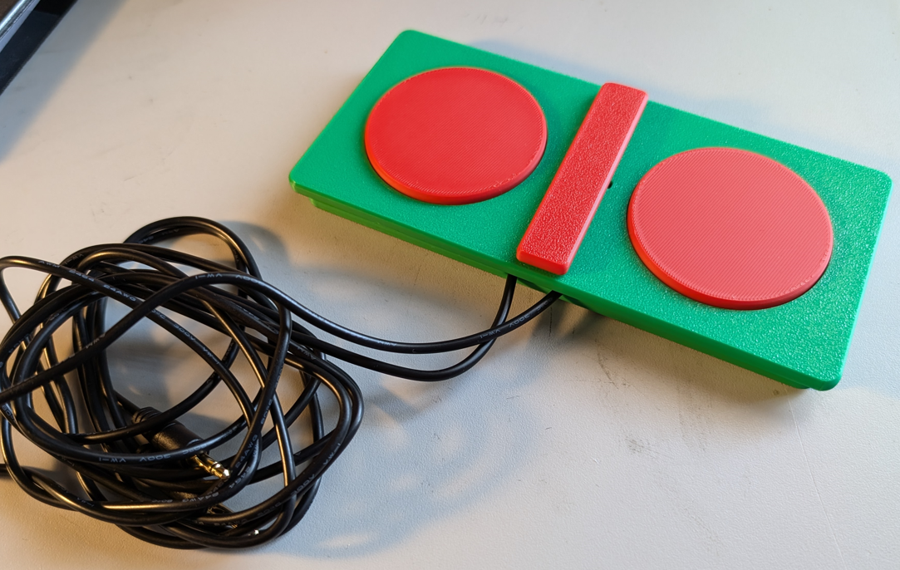
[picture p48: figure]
Assembled Open Rocker Switch

# Testing

Use a switch tester or a switch adapted device to test both of the cables coming out of the device.

# Troubleshooting

- Buttons press with a click but connected device not activating
  - If the buttons are clicking but the connected device is not activating, check the connections between the buttons and the cables. One of the connections on the button has most likely not been soldered correctly and circuit is not complete. Resolder the joints. If this does not solve the problem, try replacing the buttons with a new set.
- Buttons will not click when pressed
  - If the buttons will not click when pressed, they are most likely already pressed in the down position. Check that the buttons are flush against the bottom of the base. Things like improperly trimmed lugs or too much hot glue can raise the buttons up to the point where the neutral position of the top is enough to keep the buttons pressed down.
- Connected devices are always active
  - If the connected devices are always active but the button can still be clicked, check the connections between the cables and the wires. Look for any shorts between the leads on the buttons. A stray wire from the cables shorting between the two leads can cause the circuit to be always closed.

© 2024 by Neil Squire. This work is licensed under the CC BY SA 4.0 License: http://creativecommons.org/licenses/by-sa/4.0 Files available at https://github.com/makersmakingchange/Open-Rocker-Switch Page 1 of 1

V 2.2 | August 2024 Open Rocker Switch maker Guide

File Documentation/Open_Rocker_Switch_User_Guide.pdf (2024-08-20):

V2.2 | August 2024

## Open Rocker Switch

## USER GUIDE

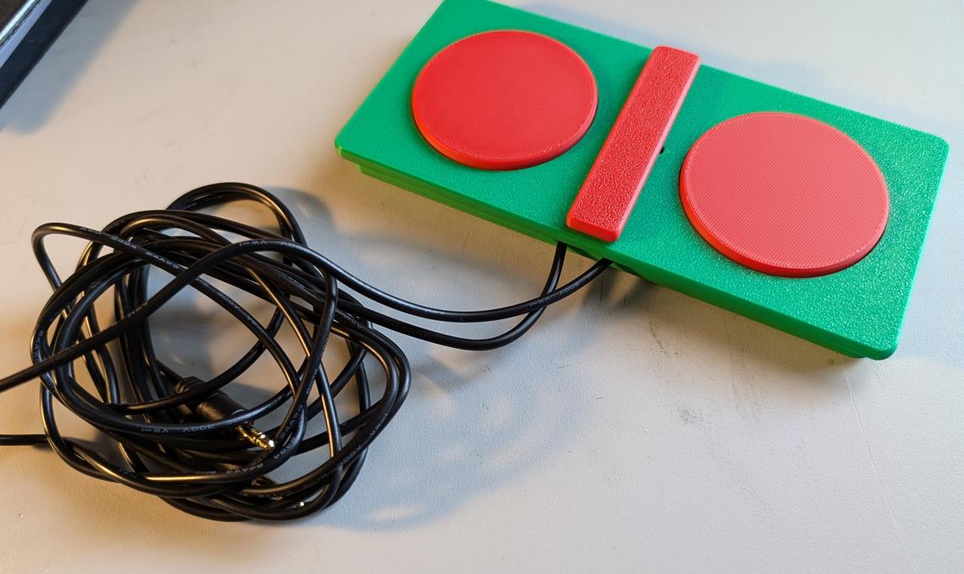
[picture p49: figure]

© 2024 by Neil Squire. (https://neilsquire.ca/)
This work is licensed under the CC BY SA 4.0 License: http://creativecommons.org/licenses/by-sa/4.0
Files available at https://github.com/makersmakingchange/Open-Rocker-Switch | Page 1 of 4

### Overview

This document contains the necessary information to use the Open Rocker Switch, a dual action accessible switch that can be activated by pressing either side of the rocker paddle. The design is based on the discontinued AbleNet Rocker Switch

## USER GUIDE

Files available at https://github.com/makersmakingchange/Open-Rocker-Switch | Page 2 of 4

## Contents

Overview | 1
Introduction | 3
Features | 3
Specifications | 3
Compatibility | 3
Usage | 4
Initial Setup | 4
Regular Use | 4
Takedown / Storage | 4
Care | 4
Cleaning | 4
Disposal | 4

## USER GUIDE

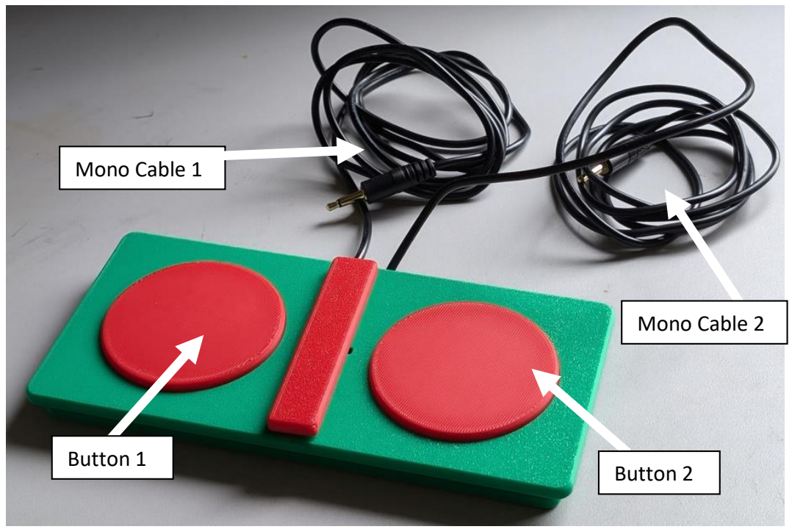
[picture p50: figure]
Button 1; Button 2; Mono Cable 2; Mono Cable 1

Files available at https://github.com/makersmakingchange/Open-Rocker-Switch | Page 3 of 4

### Introduction

The Open Rocker Switch is an inexpensive 3D printable accessibility switch. The switch consists of two separate buttons that are activated by pressing on either side. This switch is comparable in size, activation force, and travel to the discontinued AbleNet Rocker Switch. The Open Rocker Switch has interchangeable button pieces and center divider pieces for users to customize and personalize their switch.

### Features

### Specifications

Item | Open Rocker Switch
Size (Length x Width x Height) [mm] | 170x80x18mm
Mass [g] | 127g
Switch Travel [mm] | 1mm travel
Switch Force [g] | 134g

### Compatibility

The Open Rocker Switch works with any device compatible with 3.5mm accessible switches. The device works best with devices that need two switches, such as switch scanning devices.

## USER GUIDE

Files available at https://github.com/makersmakingchange/Open-Rocker-Switch | Page 4 of 4

### Usage

Initial Setup
Plug both of the mono cables from the rocker switch into the device to be controlled. The two cables come out different sides of the divider on the switch, the cable on the left side is connected to the switch on the left side and vice versa.

Regular Use
When both switch inputs are connected to the device to be used, pressing one side of the rocker switch will activate the switch to that cable. Pressing the other side of the rocker switch will activate the other switch.

Takedown / Storage
When not in use, the Open Playback Recorder should be stored in a cool place out of direct sunlight.

### Care

The Open Playback Recorder is made of 3D printed plastic. Exposure to high heat may cause warping and/or negatively affect function. Extended exposure to sunlight will also weaken the plastic on the device.

The Open Playback Recorder contains electronics and is not waterproof. If the device becomes wet, make sure it is off and do not use it until it has completely dried. It may help to open any electronic enclosures to speed up drying and ensure it has completely dried.

Cleaning
The Open Playback Recorder can be wiped with a damp cloth.

### Disposal

PLA filament may be industrially compostable in your area. Check with your waste management company if PLA can be composted or must be thrown in the garbage.

Disassemble the Open Playback Recorder and separate out the recyclable and compostable components, and those that must be thrown out. Electronics and batteries should be disposed of following your local waste management guidelines.

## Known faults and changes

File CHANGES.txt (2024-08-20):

Version 2.2| 2024-08-09
 - Changed from snap fit to pinned axle connection
 - Added cable tied and snap fits for cable management
 - Swapped button print orientation to allow for designs on the button

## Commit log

2020-12-10 Initial commit
    Adding files for version 2.0
    [ORS.f3z, ORS_Assembly.step, ORS_Bottom.f3d, ORS_Bottom.step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]
2020-12-11 Add version 1.0 files
    [ORS_BOM_v1.0.xlsx, OpenRockerSwitch_Base_v1.0.stl, OpenRockerSwitch_Top_v1.0.stl, OpenRockerSwitch_v1.0.f3d]
2020-12-11 Filename cleanup
    [ORS_BOM_v1.0.xlsx, OpenRockerSwitch_Base_v1.0.stl, OpenRockerSwitch_Top_v1.0.stl, OpenRockerSwitch_v1.0.f3d]
2020-12-11 BOM rename
    [ORS_BOM_v2.0.xlsx]
2020-12-11 Assembly rename
2022-06-14 V2.1 Upload
    This commit is replacing all the files with the 2.1 versions
    [ORS_BOM_v1.0.xlsx, ORS_Bottom.f3d, ORS_Bottom.step, ORS_Bottom.stl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]
2022-06-14 Add files via upload
    was missing version in title and BOM
    [ORS_BOM_v2.1.xlsx]
2022-06-14 Add files via upload
    minor change for capitalization
    [ORS_BOM_V2.1.xlsx]
2022-06-14 Renaming for README
    [ORS_Bottom.f3d, ORS_Bottom.step, ORS_Bottom.stl, ORS_Button_Piece.f3d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]
2022-06-14 Delete Design_Files directory
    naming was wrong
    [ORS_Bottom.f3d, ORS_Bottom.step, ORS_Button_Piece.f3d, ORS_Button_Piece.step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]
2022-06-14 Add files via upload
    updated naming for README
    [ORS_Bottom.f3d, ORS_Bottom.step, ORS_Button_Piece.f3d, ORS_Button_Piece.step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]
2024-08-20 V2.2
    Updated the design with better cable strain relief and a stronger more durable connection between the base and the top. Additionally, all documentation was updated to the new documentation package.
    [ORS_Assembly.step, ORS_BOM_V2.1.xlsx, ORS_BOM_v1.0.xlsx, ORS_Bottom.f3d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]
